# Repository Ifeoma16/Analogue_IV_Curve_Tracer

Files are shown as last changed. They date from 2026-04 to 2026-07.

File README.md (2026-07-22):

# Analogue I-V Curve Tracer Module




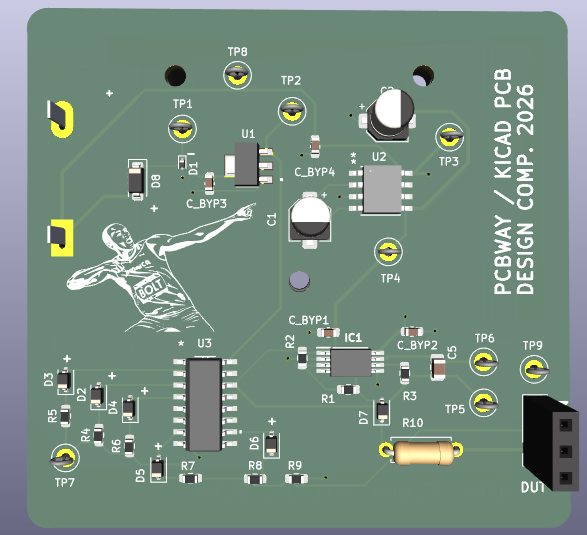
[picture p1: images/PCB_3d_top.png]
PCB_3D


An fully analogue evaluation module designed to generate characteristic I-V (current-voltage) curves for Devices Under Test (DUT) [resistors, capacitors, inductors, diodes, NPN, NMOS] using standard oscilloscope X-Y plotting. 

See Analogue_IV_Curve_Tracer.pdf file for full project report / datasheet

## 🚀 Overview
Unlike digital curve tracers, this design uses zero microcontrollers. It utilizes a synchronized hardware-only topology:
* **Base/Gate Drive:** A CD4017B decade counter configured for a 5-step staircase waveform.
* **Collector/Drain Sweep:** An op-amp integrator generating a continuous triangle wave (approx. 9V pk-pk).
* **Power Management:** 9V battery-powered with an integrated charge pump (ICL7660) for negative rail generation and ESD/Reverse Polarity protection.

---

## ✨ Key Features
- **Standalone Operation:** No firmware to flash; purely analog circuitry.
- **Precision Layout:** 4-layer PCB ($SIG \rightarrow GND \rightarrow GND \rightarrow SIG$) optimized for low-noise microamp-level current steps.
- **Multi-Component Support:** Optimized for NPN Transistors, NMOS, Diodes (including schottky, zener etc), Inductors, Capacitors, Resistors.
- **Reactive Analysis:** Capable of visualizing phase-shift loops in Capacitors and Inductors.

---

## 🛠 Hardware Specifications
| Parameter | Typical Value |
| :--- | :--- |
| **Supply Voltage** | 9V (Alkaline Battery) |
| **Sweep Frequency** | ~100 Hz |
| **Base Current Steps** | 5 Steps (approx. 10µA increments) |
| **PCB Dimensions** | 60mm x 60mm |
| **Layer Count** | 4 Layers |

---

## 📈 Sample Traces
| NPN Transistor | Capacitor (100μF) | Inductor (1H) |
| :---: | :---: | :---: |
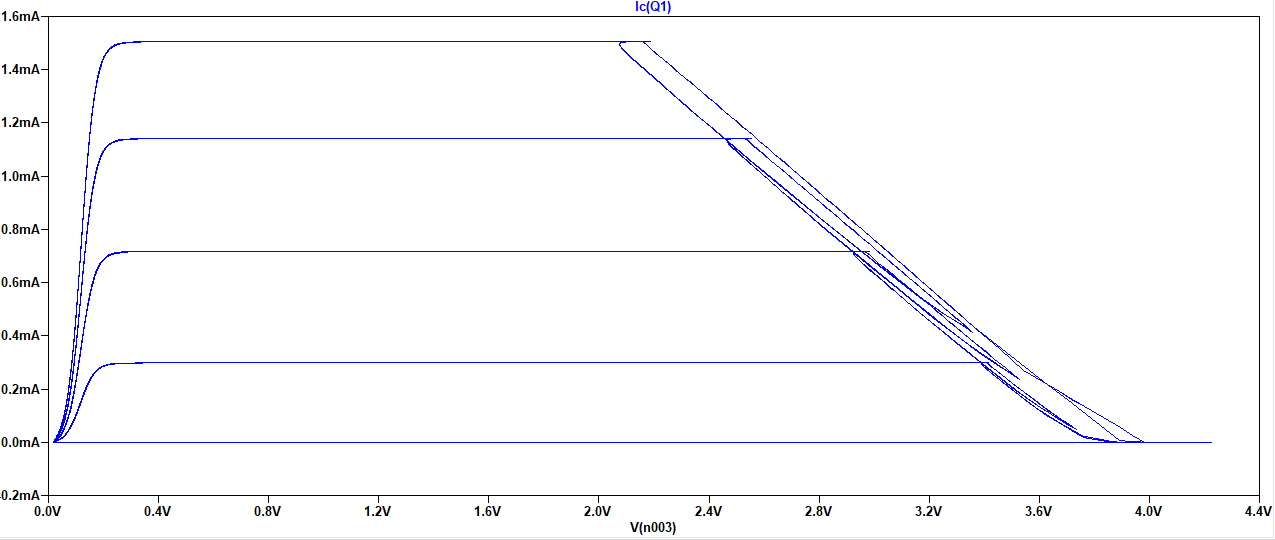
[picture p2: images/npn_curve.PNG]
NPN Trace
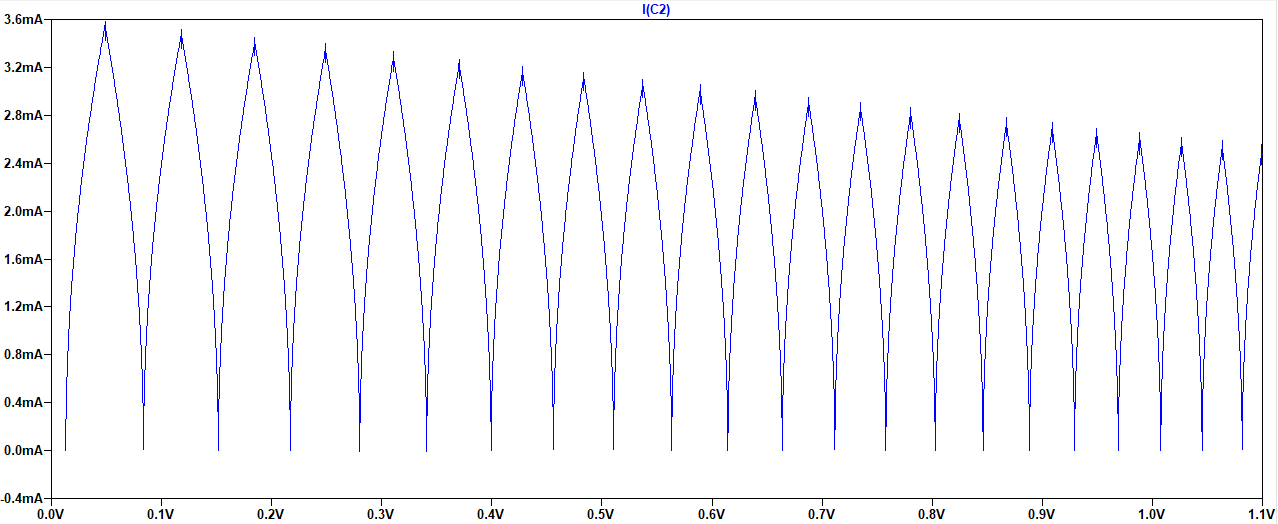
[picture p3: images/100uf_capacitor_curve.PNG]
Capacitor Trace
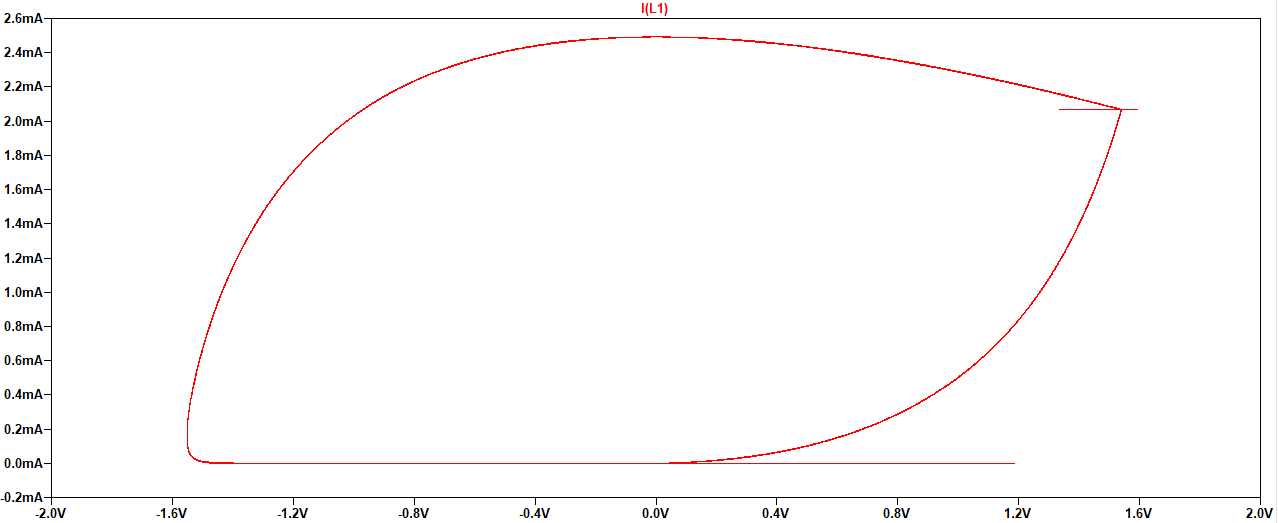
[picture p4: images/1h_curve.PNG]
Inductor Trace
|  |  |  |

---

## 🔌 Setup & Usage
To visualize curves on your oscilloscope:
1. **Power:** Connect a 9V battery to the onboard holder.
2. **Probing:** - Connect one probe (this will be X-axis) to the part of your DUT that is connected to pin 1.
   - Connect a clamp probe (this will be Y-axis)  around the wire or pin that connects your Device Under Test (DUT) to pin 1
3. **Scope Settings:** - Enable **X-Y Mode**.
   - Use XY mode to plot current vs. voltage
   - Ensure both ground clips are tied to the circuit ground.

---

## 📂 Repository Structure
* `/curve_tracer`: Full project files, including schematic, layout and fabrication files.
* `/resources`: PDFs I used for learning more on curve tracers.
* `/images`: All images used in datasheet and PCB.

---

## ⚠️ Design Limitations
- **Polarity:** This version is optimized for NPN and NMOS devices. PNP/PMOS devices will result in mirrored/inverted plots.
- **Power Dissipation:** Limited by the sourcing capability of the TL072H op-amps and the 1kΩ sense resistor.

---

## 🥚 Easter Egg
Look closely at the silkscreen: the module features **Usain Bolt**. Why? 

## 📜 References & Acknowledgments
Detailed resources used during the design phase (MIT reports, Op-amp integrator theory, etc.) are archived in the `/resources` folder.

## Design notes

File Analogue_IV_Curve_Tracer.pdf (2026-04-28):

Analogue I-V Curve Tracer Module | Rev 1.0

# Analogue I-V Curve Tracer Module

## 1 Features

- Standalone hardware topology (No MCU required)
- Synchronized 5-step staircase base current generator utilizing CD4017B logic
- Integrated triangle wave collector sweep
- 4-layer, low-noise PCB design (60mm × 60mm)
- Test Points accounted for on important nodes
- Battery holder for 9V alkaline battery
- Reverse polarity and ESD protection

## 2 Applications

- Discrete semiconductor characterization (NPN, NMOS, Diodes)
- Component matching and tolerance verification
- Educational laboratory demonstrations
- Reactive component (Capacitor/Inductor) loop analysis

## 3 General Description

The Analog I-V Curve Tracer is a compact evaluation module designed to generate standard characteristic curves for two- and three-terminal devices on any oscilloscope equipped with an X-Y mode. By utilizing a continuous triangle wave generated by an op-amp integrator and a decade counter used to generate a staircase wave, the module safely steps base current while sweeping collector voltage.
Note: Board can likely be made into 2-layers with ground plane on bottom if you would like, to save cost The 4-layer layout (SIG → GND → GND → SIG) aids signal integrity for microamp-level current steps. It is built to be powered by a 9V alkaline battery such as these (https://www.amazon.com/Amazon-Basics-Performance-All-Purpose-Batteries/dp/B00MH4QM1S?rdc=1) from Amazon.

There is a GitHub repository for this project, (https://github.com/Ifeoma16/Analogue_IV_Curve_Tracer) containing all files for the project.

Figure 0. Routing of the PCB


Figure 1. Top view of the 60x60mm assembled module.

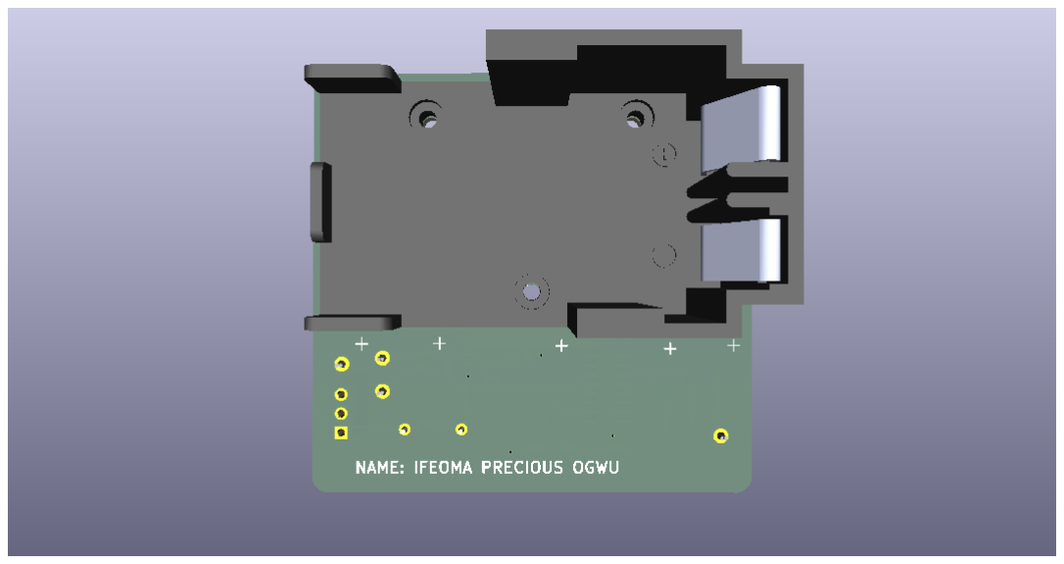
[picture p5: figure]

Figure 2. Bottom view of the 60x60mm assembled module.

## 4 Specifications

### 4.1 Absolute Maximum Ratings

Stresses beyond those listed may cause permanent damage to the device.

Parameter | Conditions | Max
Supply Voltage | Continuous | 9V
Module Power Dissipation | TA = 25◦C | 1.1 mW
DUT Power Dissipation | TA = 25◦C | 0.2 W

### 4.2 Electrical Characteristics

VCC = +9V, VEE = −9V, VDD = 5V, TA = 25◦C unless otherwise noted.

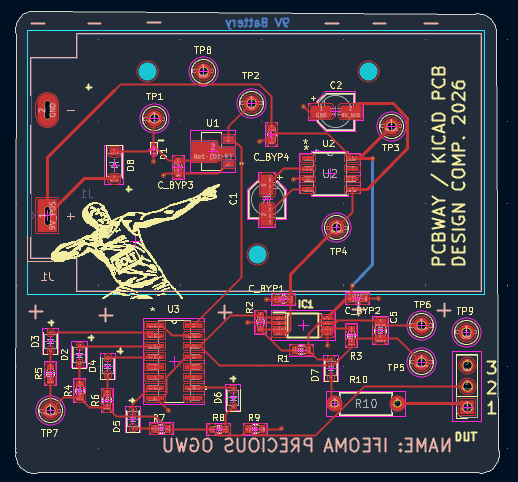
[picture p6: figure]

Ifeoma Precious Ogwu | 1 | PCBWay / KiCAD PCB Design Competition 2026

Parameter | Min | Typ | Max

Power Supply
Operating Voltage | 7V | 9V | 10V
Source Resistance | – | 55 | –
Quiescent Current | – | 2.4 mA | –

Sweep Generator
Sweep Freq. | – | 100Hz | –
Sweep Output (Vpk−pk) | – | 9V | –
Square Wave (Vpk−pk) | – | 16V | –

Base Drive
Number of Steps | – | 5 | –
Resistance | 450 | – | –
Capacitance | 10F | – | 1F
Inductance | 47mH | – | –

## 5 Detailed Description and Simulations

Simulations were conducted in LTSpice to validate design. A comparator op-amp circuit generates a 100Hz square wave that is fed into a comparator circuit generating a triangle wave. The op-amps used are the TL072H.

The square wave is fed into the clock signal of the CD4017B and the decade counter is used to generate the staircase wave. The staircase wave output is fed into a npn or NMOS (if that is the current DUT) through an external base / gate resistor.

The triangle wave is fed into a diode and resistor in series to pass only positive values of the triangle wave. This resistor connection is connected to the collector / drain of a npn or NMOS transistor of the top of a resistor, capacitor, inductor or positive side of a diode (schottky, zener etc) depending on the DUT.

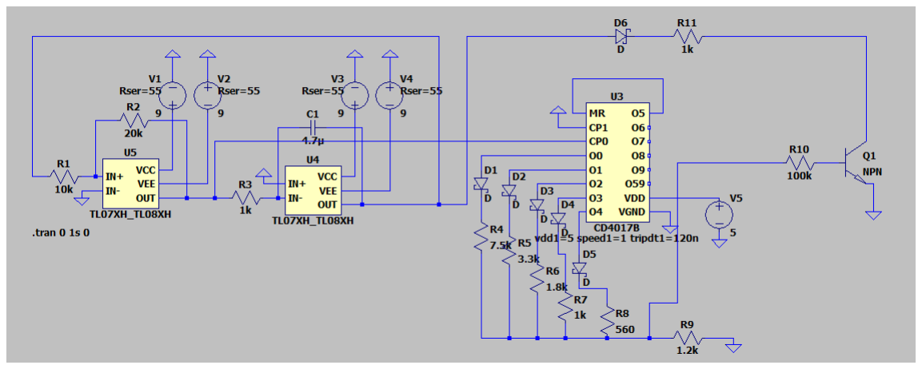
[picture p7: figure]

Figure 3. LTSpice Simulation.

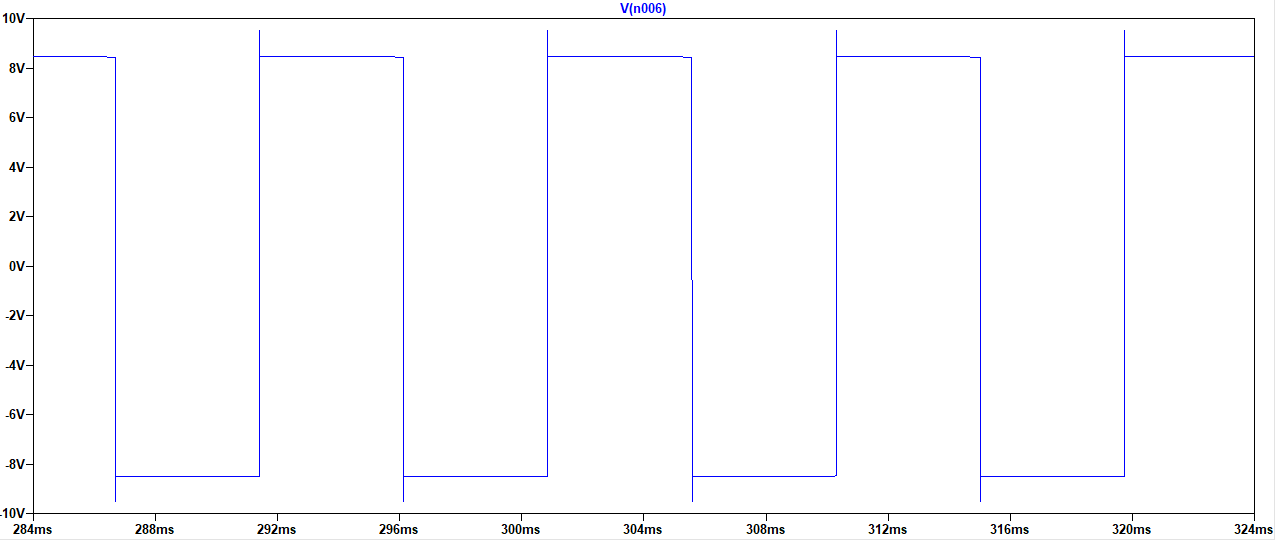
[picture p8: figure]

Figure 4. Square Wave From Simulation.

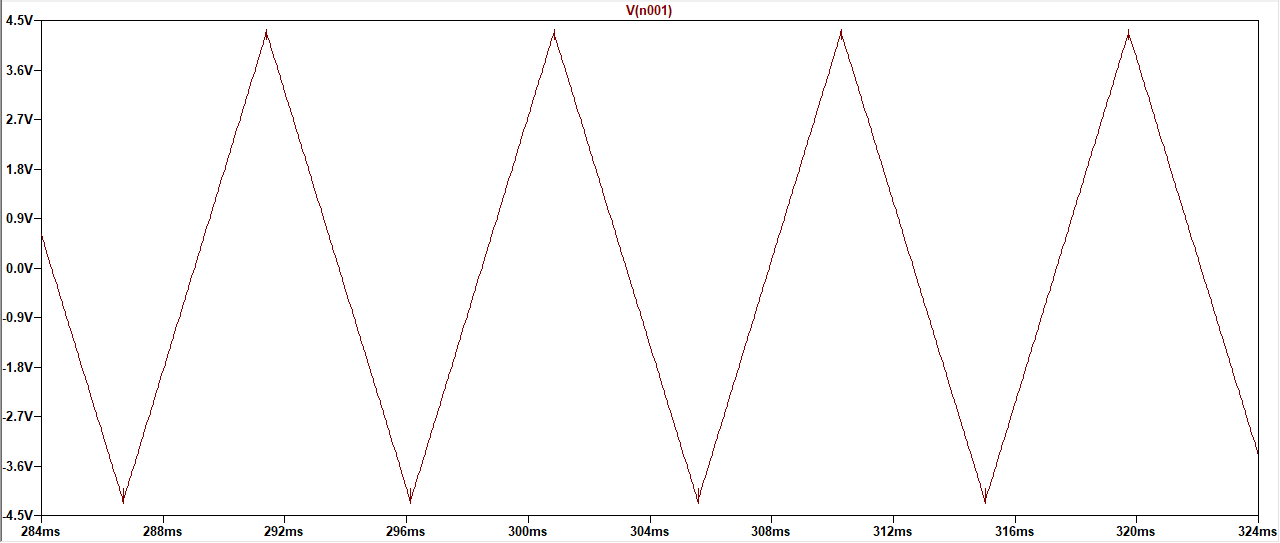
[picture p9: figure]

Figure 5. Triangle Wave From Simulation.

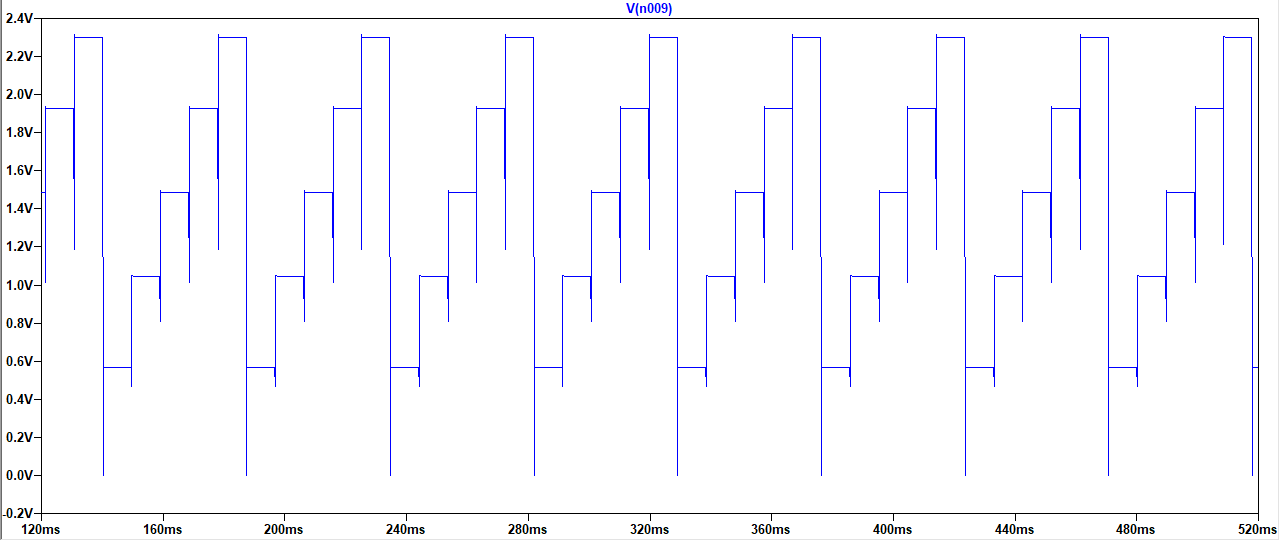
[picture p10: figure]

Figure 6. Staircase Wave From Simulation.

For the PCB:

The 9V battery is connected through a 1N5817 diode, used for reverse polarity protection, then a 11V TVS diode is connected from the cathode of 1N5817 to ground for ESD protection.
The line continues then to connect to the 5V LDO HT7350-A used to connect to VDD of the CD4017B. The 9V battery is also connected to an ICL7660 charge pump that gives us -9V which we can use ±9V for the op-amp. From there, the connections are basically same as in LTSpice. There are 0.1 bypass capacitors added to the input pins of the ICs to reduce / prevent noise.
The outputs of the entire circuit needed for the DUT is connected to a 3-pin 2.54mm header socket. There are also test points placed, that can be used for debugging or other purposes.

Note: There’s errors in DRC due to the components being on top of the battery holder. However, looking sideways, you can solder and cut the excess off enough to not interfere

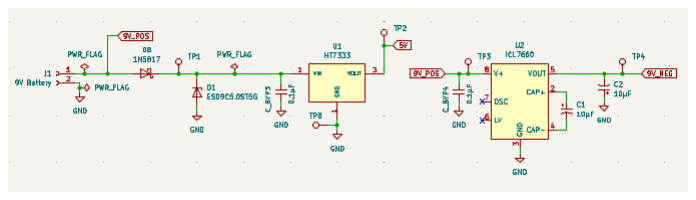
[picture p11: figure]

Figure 7. Positve and negative 9V generation, as well as 5V.

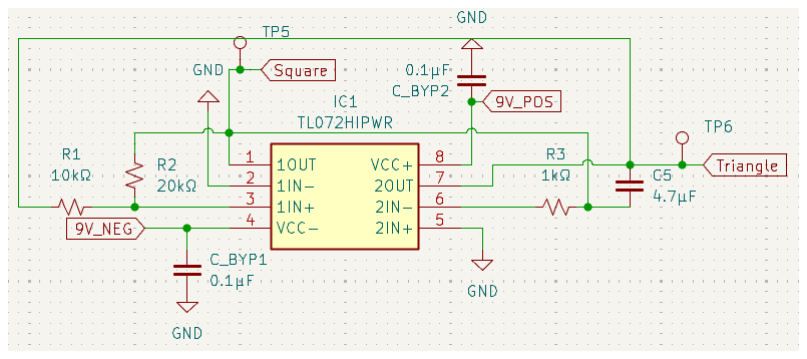
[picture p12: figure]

Figure 8. Square and triangle wave generation from op-amps.

Ifeoma Precious Ogwu | 2 | PCBWay / KiCAD PCB Design Competition 2026

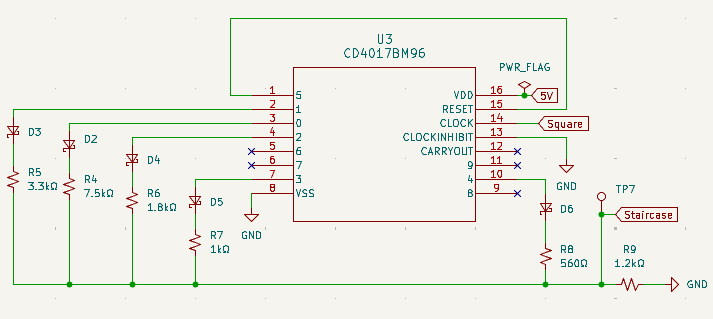
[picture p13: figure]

Figure 10. Staircase wave generation from decade counter.

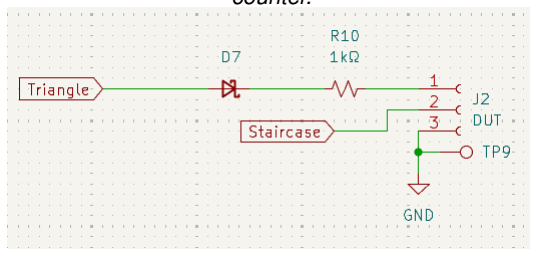
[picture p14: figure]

Figure 11. Outputs for DUT.

## 6 Naming

For use of this module, these are the relevant pins and their uses:
- TP1: 9V (positive). Placed in a such a way, it can be used to verify if the D8 is working properly and in right direction.
- TP2: 5V
- TP3: 9V (positive)
- TP4: 9V (negative)
- TP5: Square wave
- TP6: Triangle wave
- TP7: Staircase wave
- TP8: GND
- TP9: GND. This test point is located next to the DUT socket so you can use to ground your oscilloscope probe.

For the 3-pin socket that you can place your DUT into:

- 1: Connected to the series diode and 1k resistor connected from the triangle wave to the ”top” of the DUT
- 2: Staircase wave output. Use for NMOS and npn.
- 3: GND

## 7 Hardware Interface

How to connect each DUT:

### 7.1 Resistor

- Connect one end of the resistor to R10 and the other end to GND.

### 7.2 Capacitor

- Connect one end of the capacitor (if polarized, connect the positive) to R10 and the other end to GND

### 7.3 Inductor

- Connect one end of the inductor to R10 and the other end to GND.

### 7.4 Diode

- Connect the anode (positive) of the diode to R10 and the cathode (negative ) to GND.

### 7.5 npn

- Connect the collector to R10, connect the base to an external resistor which you then connect to pin 2 of the DUT socket, connect the emitter to GND.

### 7.6 NMOS

- Connect the drain to R10, connect the gate to an external resistor which you then connect to pin 2 of the DUT socket, connect the source to GND.

How to connect DUT to oscilloscope:

If you have a probe that can measure current such as this (https://www.amazon.com/Hantek-Transducer-Multimeter-Oscilloscope-Connector/dp/B08KZMS4Z2) (any products links in this document are not recommendations or endorsements [unless they are the ICs and components used in the PCB], they are simply examples) from Amazon then:

- Connect one probe (this will be X-axis) to the part of your DUT that is connected to pin 1.
- Connect a clamp probe (this will be Y-axis) around the wire or pin that connects your Device Under Test (DUT) to pin 1
- Use XY mode to plot current vs. voltage
- GND: Ensure oscilloscope ground clips are tied strictly to the board’s designated common ground to prevent shorting.

If you do not have a current clamp probe:

- Connect a small shunt resistor (eg 0.1 or 1) in series with pin 1 to your DUT. You maybe just use the on-board R10 as your shunt. This has not been tested yet, however.
- Connect a probe (this will be Y-axis) to one side of the resistor and the ground clip to the other. (Note: Ensure the ground clip is connected to the side closest to ground to avoid shorting your circuit, or use a differential measurement.)
- On the oscilloscope, use the Math function to divide the channel voltage by the shunt resistance value.
- Connect another probe (this will be X-axis) to the part of your DUT that is connected to pin 1.
- Use XY mode to plot current vs. voltage
- GND: Ensure oscilloscope ground clips are tied strictly to the board’s designated common ground to prevent shorting.
Ifeoma Precious Ogwu | 3 | PCBWay / KiCAD PCB Design Competition 2026

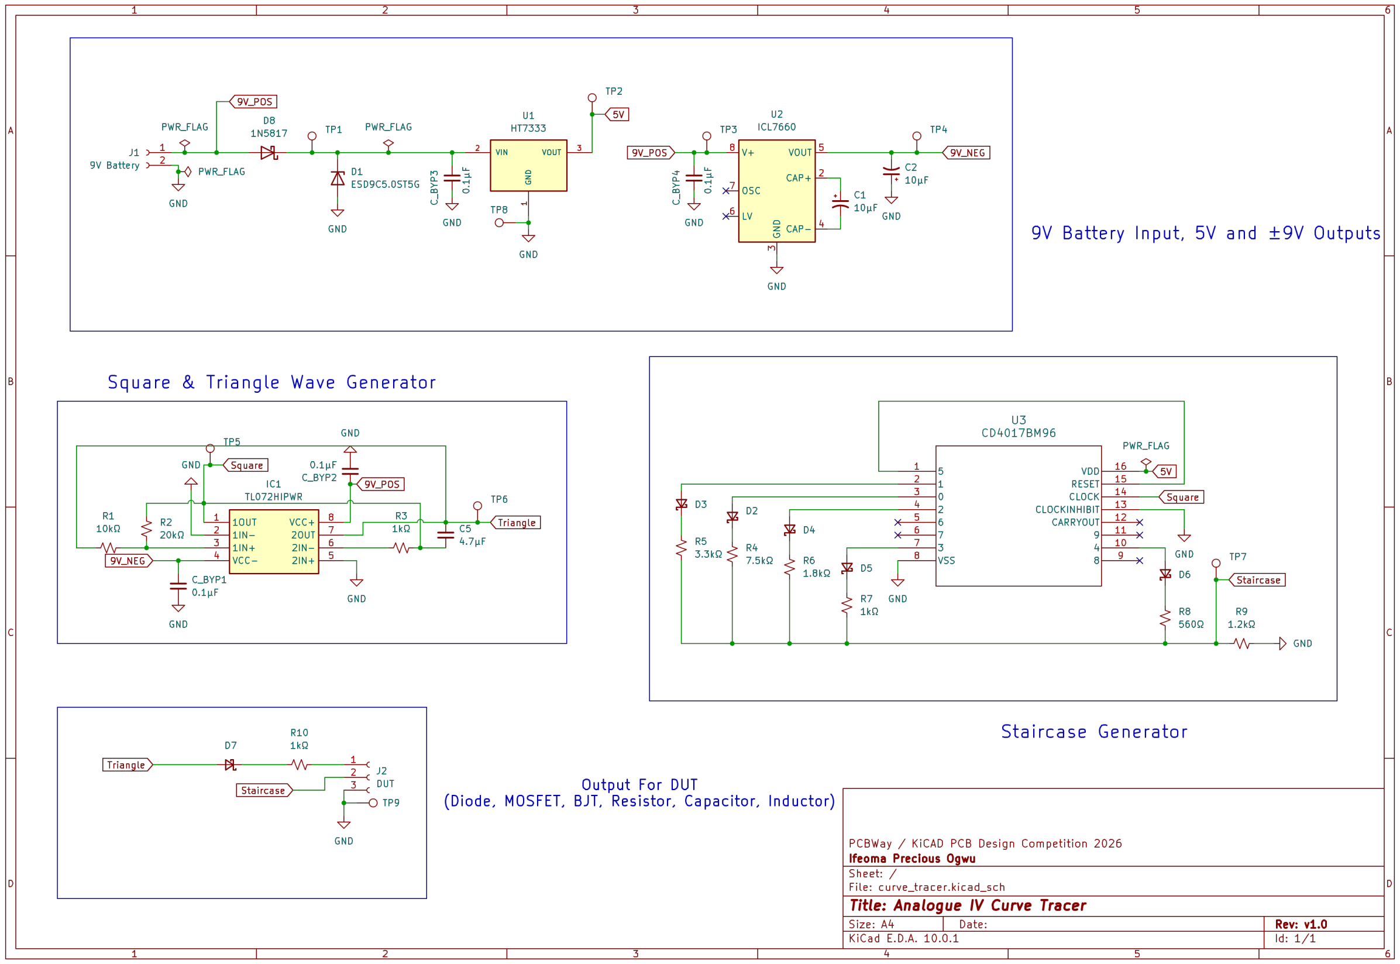
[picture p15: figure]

Figure 1: Figure 12. Full KiCAD Schematic

Ifeoma Precious Ogwu | 4 | PCBWay / KiCAD PCB Design Competition 2026

## Typical Performance Characteristics

The following waveforms represent typical operation using standard off-the-shelf components.


Figure 13. NPN Transistor Characteristic Sweep (Ic vs

Vce).

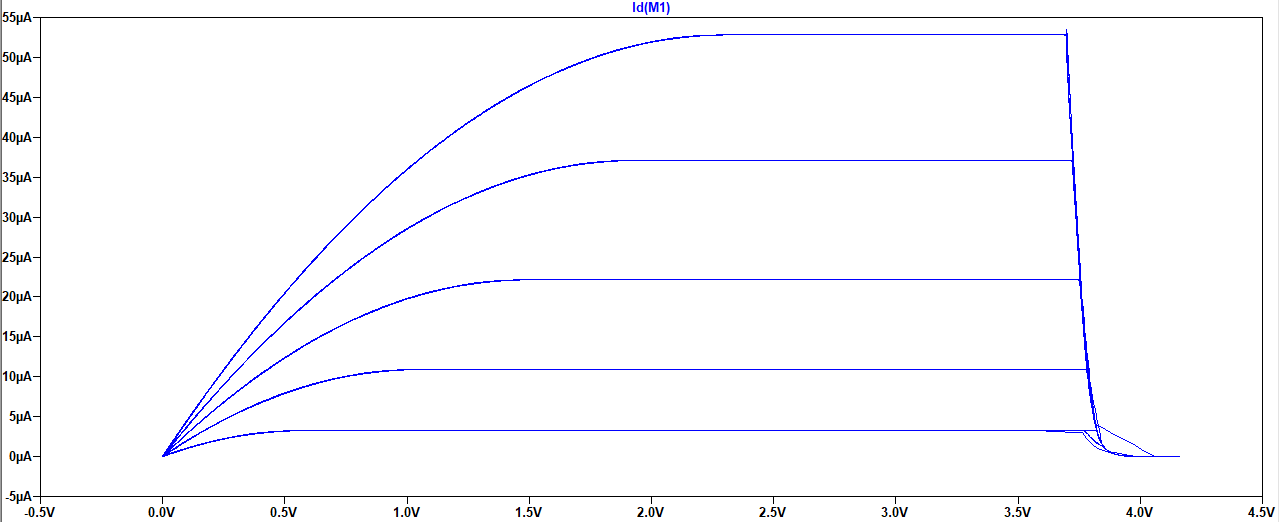
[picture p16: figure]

Figure 13. NMOS Transistor Characteristic Sweep (IG vs

VDS).


Figure 15. Reactive Load Analysis: 100µF Capacitor showing expected curve


Figure 16. Reactive Load Analysis: 1H Inductor showing standard elliptical response.

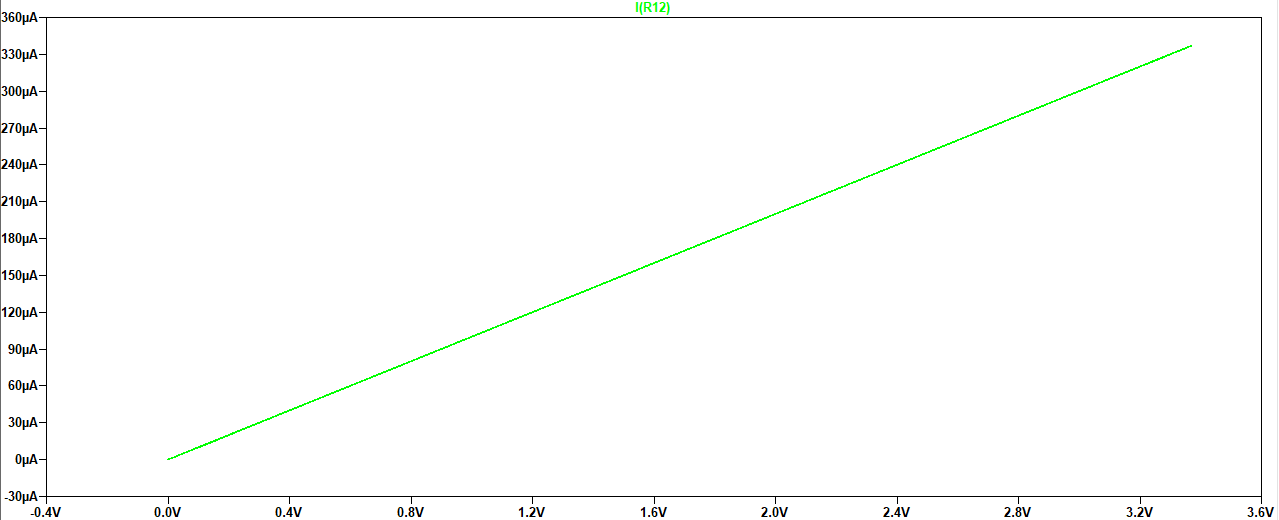
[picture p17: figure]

Figure 17. 10k resistor showing expected straight-line
graph.

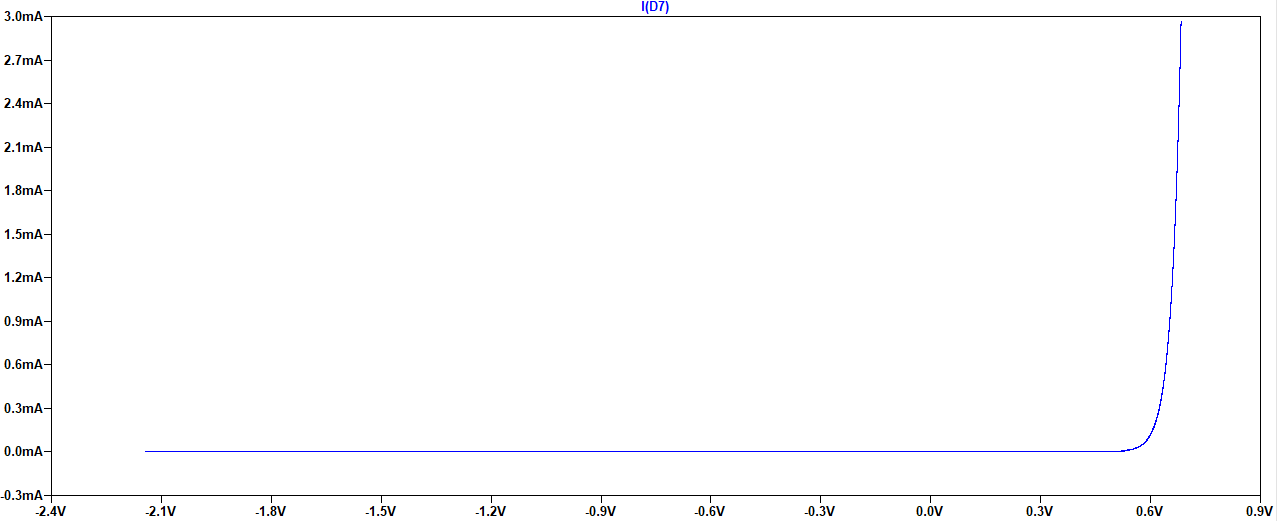
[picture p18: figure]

Figure 18. Diode showing expected curve.

Ifeoma Precious Ogwu | 5 | PCBWay / KiCAD PCB Design Competition 2026

## 8 BOM

The components were selected for a balance between high functionality and lower costs. The current BOM costs a total of $11.88 USD = 8.82 = 10.16 = $16.24 CAD = $207.24 MXN. The components were mainly sourced from DigiKey. There are also components sourced from LCSC and Amazon. You can source components from wherever you please, as long as it is the same footprint and make for the main ICs and as long as you are fine with your selected tolerances for capacitors and resistors.
Note: All resistors are 0.5W rated. You can get resistors rated for more power, but it is not recommended to get resistors rated for lower power.

The BOM is posted on the GitHub page for this project. (https://github.com/Ifeoma16/Analogue_IV_Curve_Tracer)

## 9 Design Limitations

While optimized for standard NPN and NMOS topologies, this hardware revision utilizes a unidirectional positive voltage sweep. Consequently, PNP and PMOS characterization will result in inverted/mirrored plots and may not fully forward-bias internal junctions correctly.
You are welcome to attempt to rectify this issue.

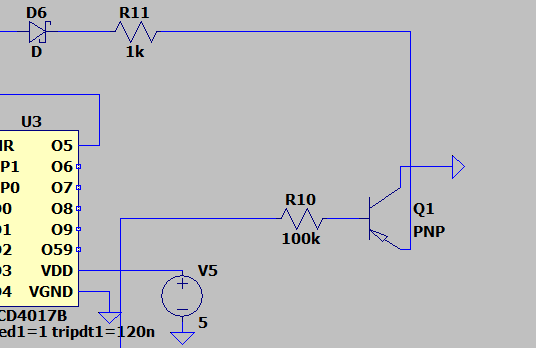
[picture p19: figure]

Figure 19. LTSpice Setup For pnp Or PMOS

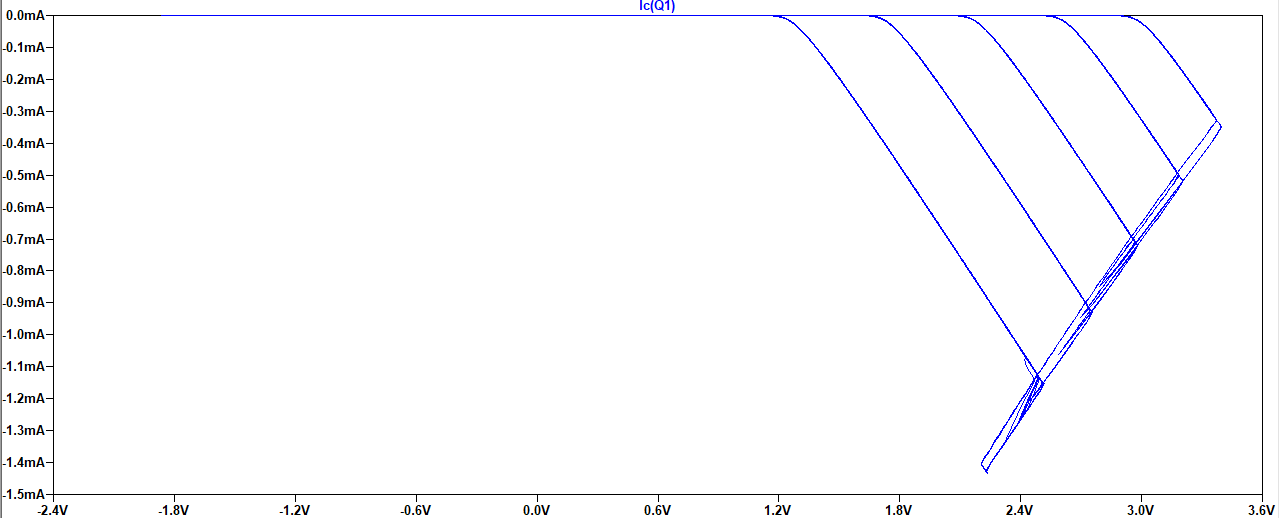
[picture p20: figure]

Figure 20. pnp curve.

Figure 21. PMOS curve.

Easter Egg: Why did I choose Usain Bolt specifically on my silkscreen?

## 10 Concluding Notes

Here are some of the resources I used to learn more about how to design and build a curve tracer:
- Building A Curve Tracer (https://www.paulvdiyblogs.net/2017/12/building-curve-tracer.html)
- Building A Curve Tracer v3 (https://www.paulvdiyblogs.net/2021/03/building-curve-tracer-version-3.html)
- Design & Build a Stair-Step Waveform Generator (http://www.scullcom.uk/design-build-a-stair-step-waveform-generator/)
- Analog Curve Tracer - MIT Report (https://web.mit.edu/6.101/www/s2020/projects/merni_Project_Final_Report.pdf)
- Op-Amp Comparator Circuit (https://www.electronics-tutorials.ws/opamp/op-amp-comparator.html)
- Op-Amp Integrator Circuit (https://www.electronics-tutorials.ws/opamp/opamp_6.html)

Most of the websites are in pdf format on the GitHub page for this project. (https://github.com/Ifeoma16/Analogue_IV_Curve_Tracer)

Using the online PCBWay instant quote:

For a PCBA, each board would cost about $29 Without PCBA, each board would cost about $17

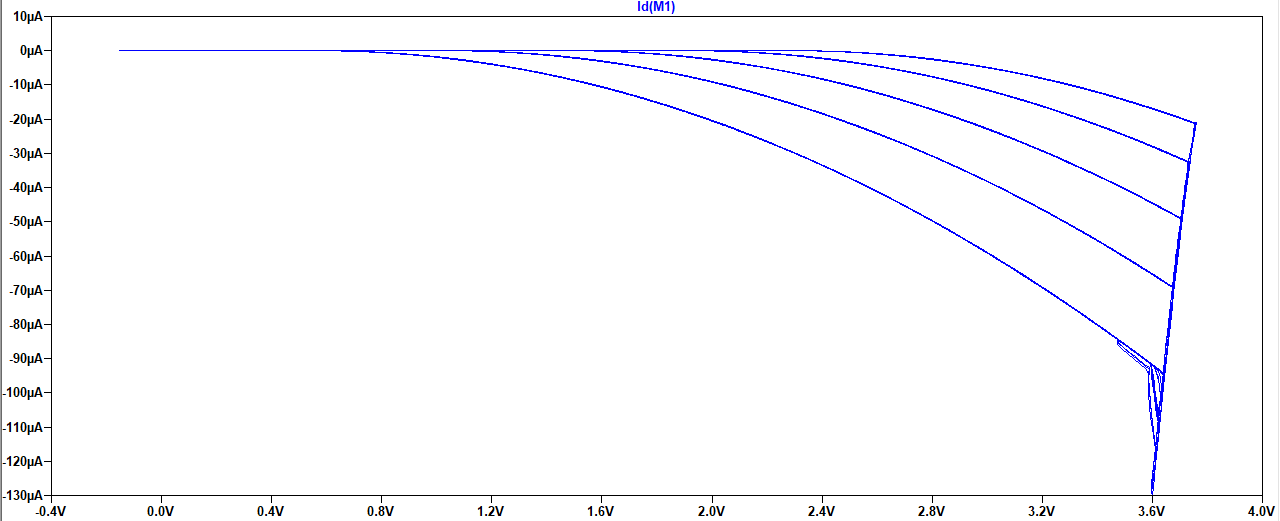
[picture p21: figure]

Ifeoma Precious Ogwu | 6 | PCBWay / KiCAD PCB Design Competition 2026

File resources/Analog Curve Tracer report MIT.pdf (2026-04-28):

# Analog Curve Tracer

### Makita Erni, Gregory Xie

### May 12, 2020

## Contents

1 Abstract | 3
2 Project Overview | 3
3 Design | 4

4 PCB Layout | 16
5 Conclusion | 21

## 1 Abstract

In order to preemptively replace the aging curve tracers in the 6.101 lab, we decided to design a replacement for our final project.

A replacement device should be able to replace the Tektronix 575 in the context of 6.101. This means that it has to be able to generate characteristic curves for BJTs and diodes. Users should be able to easily adjust testing parameters to fit the device being tested, and it should be easy to view and capture the generated curves.

Our design can automatically identify whether the device under test (DUT) is a bipolar junction transistor or a two-terminal device, like a resistor or a diode. If the device is a BJT, it also detects the type (NPN or PNP), as well as its orientation. Based off of this information, it sets up the test and applies the test currents in the appropriate directions. The BJT testing only works if the middle pin is the base, but that is usually the case, so it shouldn’t be a problem. Users can adjust various testing parameters through 3 rotary switches.

The output of the curve tracer can be read off of two test points and an oscilloscope in X-Y mode can be used to display the curves generated. This allows for the easy export of the characteristic curves through the oscilloscope’s USB port.

## 2 Project Overview

Our project’s circuit can be split into three main parts - the device identification circuit, the control voltage generation circuit, and the two voltage controlled current sources used to test the DUT.

The device identification circuit determines how the testing setup for the DUT should be setup, and includes an array of analog switches in order to connect the device in the way required for testing. The device identification circuit also provides the control voltage generation circuit with two voltages representing the directions of the base and collector currents.

The control voltage generation circuit uses these two voltages, as well as inputs given from the user through three rotary switches, to generate a staircase wave that controls the base current source, and a triangle wave that controls the collector current source. The commanded current is proportional to the voltage.

Finally, the two current sources reference the control voltages to test the DUT by pushing or pulling current through the device. Voltages representing the current through the device and the voltage across the device are available for the user to probe through test points.

## 3 Design

### 3.1 Overall System Design

The design involves a discrete sweep of the base current and a continuous sweep of the collector current which was accomplished with two voltage controlled current sources.

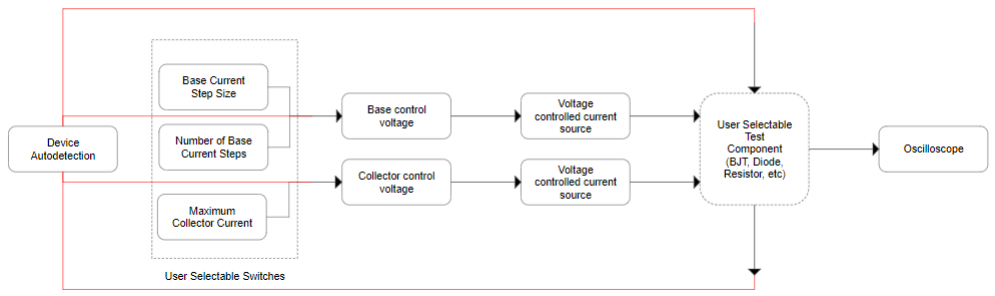
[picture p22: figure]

Figure 1: Overall Block Diagram

### 3.2 User Input

User input for setting the base current step size, number of base current steps, and the maximum collector current is taken through 10 position rotary switches. The switches for base current step size and maximum collector current change the gain of an amplification stage by changing the feedback resistor of an inverting amplifier. The switch for number of base current steps changes the value of a resistor in a voltage divider, changing a reference voltage.

### 3.3 Automatic Device Identification

### 3.3.1 Theory

This section of the circuit needs to determine if the DUT is a BJT or a two-terminal device, as well as determine the type and pin orientation for BJTs.

Because BJTs are constructed by sandwiching one semiconductor type between two layers of another, each has two junctions, and thus look like two diodes from the perspective of the base.

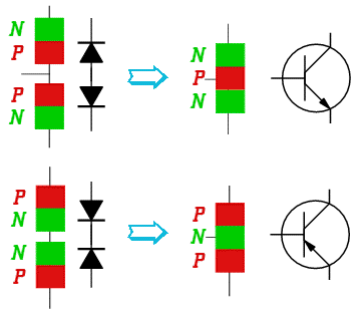
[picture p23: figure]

Figure 2: BJTs can be identified because they can look like two diodes from the perspective of the base. Source: http://fourier.eng.hmc.edu/e84/lectures/ch4/node3.html

A BJT can be identified by looking for these diode drops when the emitter and the collector are grounded through resistors, and a test voltage is applied to the base. For a PNP type BJT, the diode drops will appear when the test voltage is negative. For a NPN type BJT, the diode drops will appear when the test voltage is positive. When the test voltage is the wrong polarity for the type of device, the voltage drop will be the full test voltage. This allows for the identification of the type of device.

Because of differences in doping concentration (the emitter region is typically doped more heavily than the collector), the base-emitter diode drop is typically larger than the base-collector diode drop. This allows for the identification of these two pins.

Both of these methods require knowledge of which pin is the base of the device. Because this is the center pin for the BJT packages available in the lab, this was assumed to be known.

### 3.3.2 Implementation

The electronics that implement the device identification circuit consists of a sawtooth wave generator, window comparators, XOR gates, S/R latches, and opamp subtractors. The circuit controls an array of analog switches used to set up the testing conditions for the device.

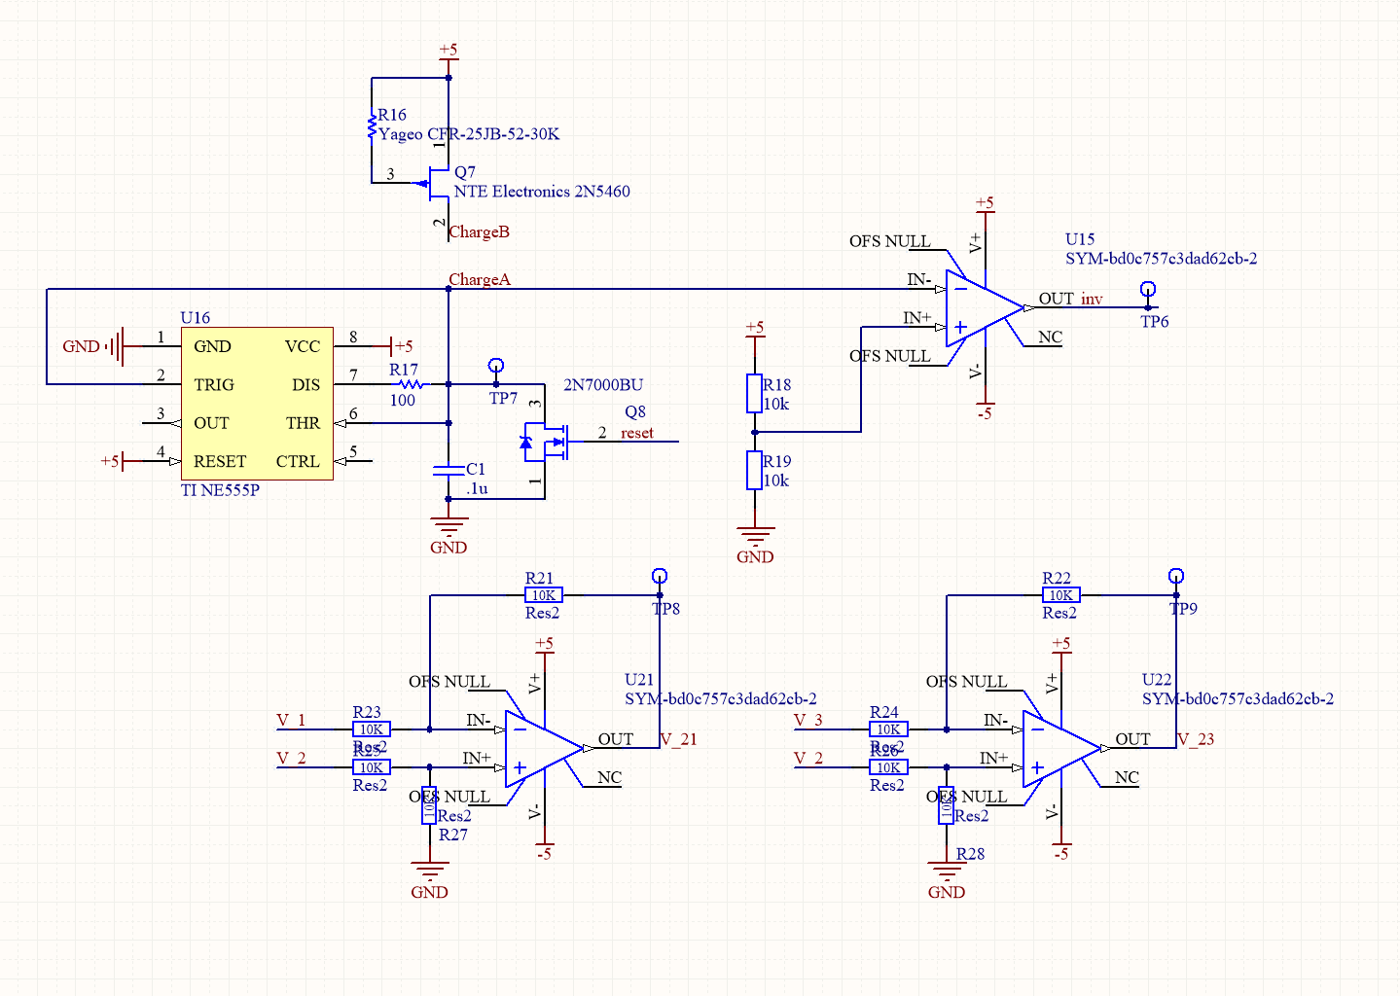
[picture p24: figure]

Figure 3: Sawtooth Generator, Subtractors, and Test Voltage Opamp

The sawtooth generator is implemented with a 555 timer set up in an astable configuration, with the timing capacitor driven by a JFET (2N54560) current source. The JFET current source is connected to the timing capacitor through an analog switch, which allows the circuit to hold the sawtooth voltage by disconnecting the current source. A NMOS (2N7000) connected in parallel with the timing capacitor allows the circuit to reset the sawtooth.

Each window comparator is made from two LM211s, which were chosen for their lower offset voltage when compared to the more common LM311. The reference voltages for the two comparators are set through a three tap resistor divider. By adjusting the values of the resistors in the divider, you can change the range of voltages in which the window comparator will output a logic high. As the output of the comparators are open-collector, they are pulled up to the positive supply rail through a resistor, and are tied together. The other comparators in the design are also LM211s.

Due to PCB size constraints, we opted to use integrated circuits to implement the XOR gates and S/R latches. For the XOR gates, the CD4043B was used, and for the S/R latch, the SN74LS86A was used. Both were chosen because they were not clocked, and were available in through hole packages. S/R latches were chosen instead of a sample-and-hold circuit because they were needed to reset the staircase wave used in the base control voltage, and many integrated circuits had multiple latches available. We can control when these latches sample the input by pulling the set pin to ground, and releasing it when we want to sample.

For the analog switches, we used the ADG441/ADG442 CMOS switches for all the switching where the resistance was not critical. These switches were used instead of MOSFETS because in a lot of the situations where switching is needed, the voltage at the source changes, which makes it hard to turn the MOSFET completely on. Using analog switches simplifies the

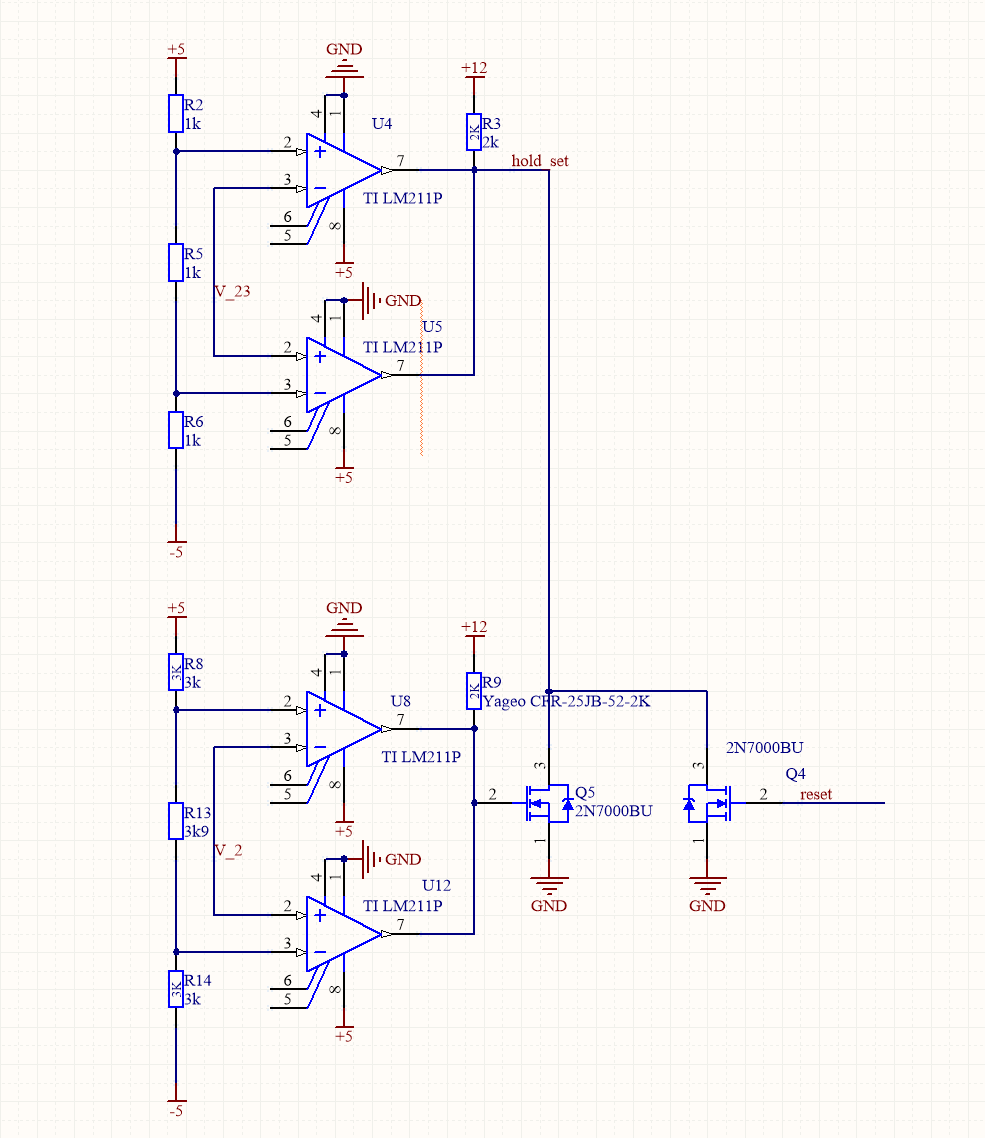
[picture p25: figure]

Figure 4: Window Comparator

design greatly, and allows us to switch both positive and negative voltages. To connect the DUT to our testing circuit, we used the MAX4663, which has a much lower on resistance (2.5 Ω), and guarantees break-before-make switching, allowing us to use them as multiplexers.

### 3.3.3 Operation

The sawtooth wave generator controls the entire device identification cycle, with different portions of the wave corresponding to different tests that the circuit performs. When the circuit has successfully identified a device, the circuit holds the sawtooth voltage constant while the device is being tested by disconnecting the JFET current source. Once testing is over, the sawtooth voltage is reset to 0 and the cycle restarts. Throughout the entire device identification cycle, the pins 1 and 3 are grounded through resistors. This is done through analog switches.

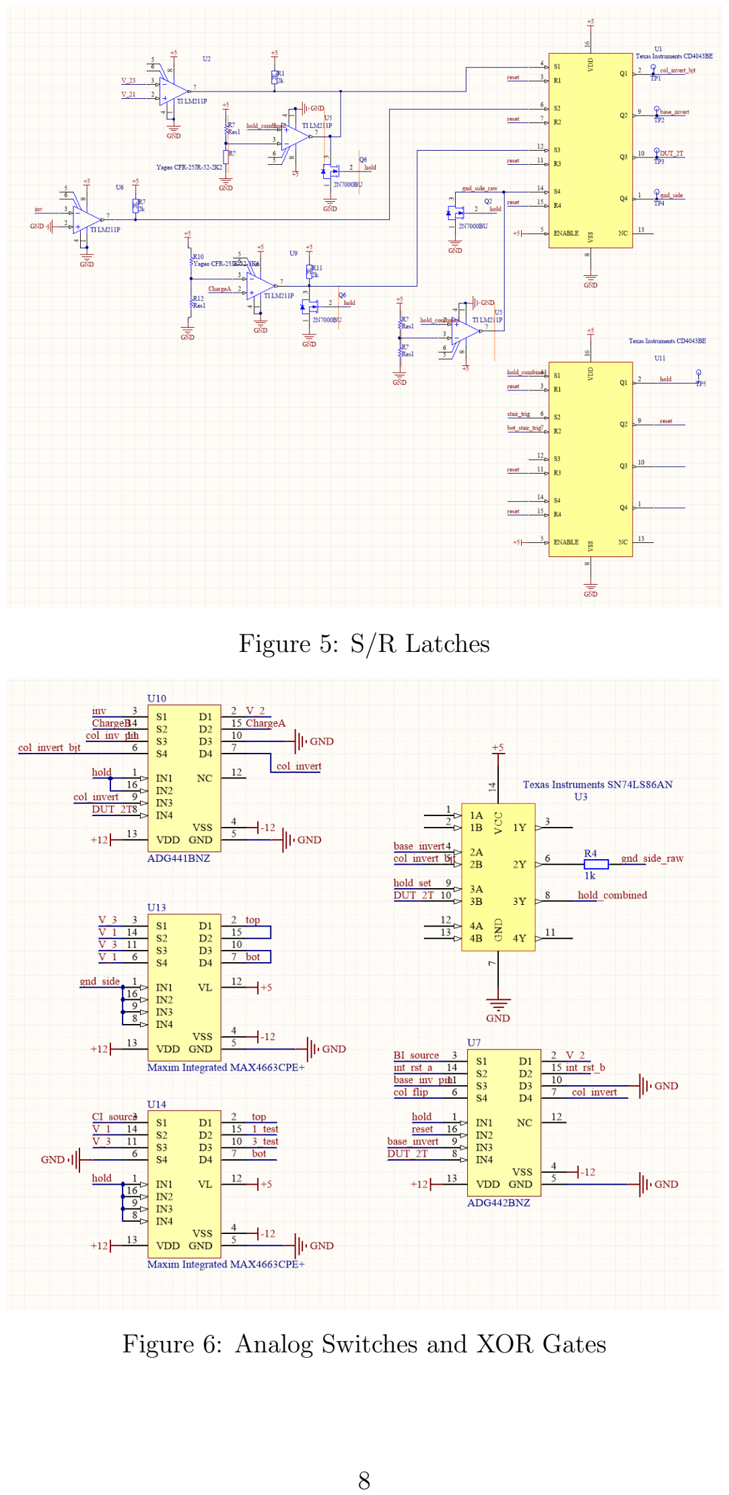
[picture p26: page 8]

Figure 5: S/R Latches

Figure 6: Analog Switches and XOR Gates

Throughout the entire testing period, the voltage drop between pins 2 and 3 (V2,3), as well as the voltage drop between 2 and 1 (V2,1) are measured. These two voltages are fed into a comparator that goes high when V2,1 > V2,3. This result can be XORed with the output of a comparator representing the inverse of the test voltage (high if negative test voltage, low if positive voltage) to produce a voltage which pin is the emitter of the device, which should be grounded during the testing cycle (GND Side). The inverse of the test voltage represents whether current should be pushed or pulled out of the base, as well as whether current should be pushed or pulled out of the collector. These values sampled and held in S/R latches when the device identification cycle ends and the testing cycle begins. These two voltages are used as inputs to an array of analog switches that connect the DUT to the testing setup in the correct way, and determine if the base and collector control voltages are inverted or not.

These relations can be seen in Table 1.

Device Identification Truth Table
V2,1 > V2,3 | Vtest < 0 | Collector and Base Current Direction | GND Side
1 1 0 0 | 1 (PNP) 0 (NPN) 1 (PNP) 0 (NPN) | 1 (Pull) 0 (Push) 1 (Pull) 0 (Push) | 0 (Pin 1) 1 (Pin 3) 1 (Pin 3) 0 (Pin 1)

Table 1: Truth Table relating measured values to testing parameters

For the first third of the sawtooth, the circuit checks to see if the DUT is a NPN BJT by applying 5V to pin 2. If −1.66 < V2,3 < 1.66, and (Vtest > 2 or Vtest < 2), the HOLD latch is set, the sawtooth voltage is held, and the device is tested using the parameters determined from the circuit. This ends the device identification cycle and starts the testing cycle.

For the middle third of the sawtooth, the circuit checks if the DUT is a PNP BJT by applying a negative voltage (-5V) to the base. V2,3 and the test voltage are checked again, and if the device passes, the device is tested.

If both of these tests fail, the sawtooth is allowed to reach its peak. When this happens, the device identification circuit assumes that the DUT is a two-terminal device. This sets a latch corresponding to this specific device type, which in turn connects the output pin of the 555 used for the triangle generation to the control pin of the analog switch used to invert the triangle wave. This inverts the control voltage waveform halfway through the sweep, switching the test current from positive to negative, and allowing for the full testing of diodes and resistors. When testing these devices, the middle pin remains unconnected.

### 3.4 Control Voltage Generation

The control voltage generation is accomplished by two parallel circuits, one that makes triangle waves for the collector current source, and one that makes a staircase wave for the base current source. Both of these circuits are triggered by a pulse generator, which allows the collector current sweeps to be aligned with a base current step.

### 3.4.1 Pulse Generator

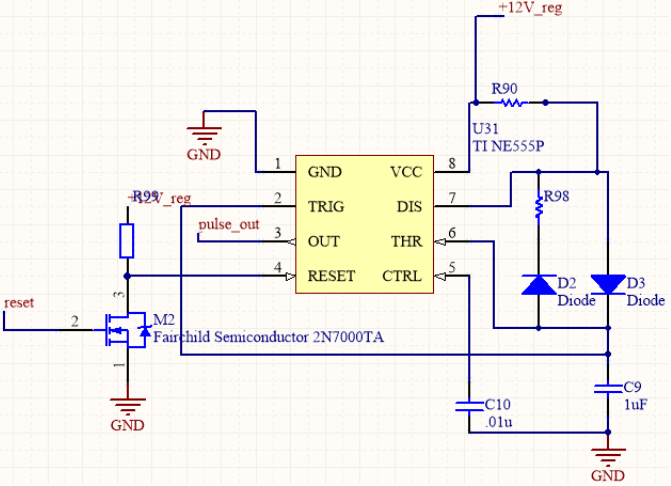
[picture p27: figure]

Figure 7: Pulse Generator Circuit

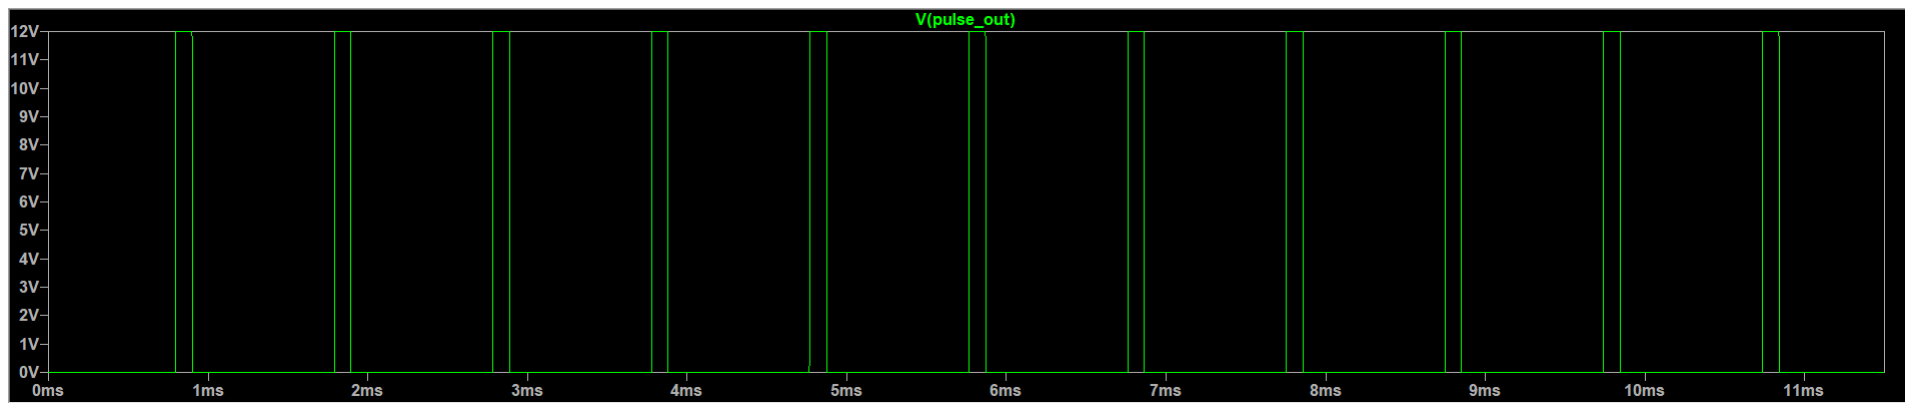
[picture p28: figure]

Figure 8: Pulse Generator Output Waveform

The pulse generator is implemented with an astable 555 timer circuit, with separate charging and discharging paths for the capacitor gated by diodes. This allows for a low duty cycle and easy control of the on and off times. The reset pin is held high when HOLD is high, signaling a testing cycle and enabling the 555 timer.

### 3.4.2 Staircase Wave Generation


Figure 9: Staircase Wave Generator Circuit


Figure 10: Example Staircase Waveform

The staircase wave is generated by integrating the pulses from the pulse generator using an opamp integrator. Once the staircase reaches a threshold voltage set by the user, the RESET S/R latch is set and the charge out of the integrating capacitor is drained out through an analog switch. When the voltage across the capacitor is close to 0V, the latch gets reset and the integrator is re-enabled. This allows the user to set the number of steps in the base current sweep.

Following the integrator, the wave goes through a unity-gain inverting/non-inverting opamp stage, where the wave can be inverted by pulling the non-inverting terminal of the opamp to ground. This stage is controlled by the device identification circuit through an analog switch. After this stage, the staircase goes through an inverting amplifier, where the gain is set by the user. This allows the user to control the size of the base current steps. The resulting waveform is fed to the base current source.

### 3.4.3 Triangle Wave Generation


Figure 11: Triangle Wave Generator Circuit


Figure 12: Example Triangle Wave

The triangle wave is generated using a monostable 555 timer circuit, with roughly equal charging and discharging times. One charge-discharge cycle of the timing capacitor happens in the period between pulses from the pulse generator. The pulses from the pulse generator are inverted and differentiated using an passive RC differentiator to act as the trigger for the circuit. This triggers the circuit on the falling edge of the pulse, which allows the base current to stabilize before the collector current sweep starts. The shape of this wave is not critical, and so a constant current source was not needed to charge the capacitor.

The output is taken across the timing capacitor, buffered and then sent through an identical set of processing stages. For the triangle wave, adjusting the gain of the inverting stage allows users to change the maximum current sent through the device.

### 3.5 Voltage Controlled Current Sources

The voltage controlled current sources consist of two circuits. One is connected to the pin 2 of the DUT and is controlled by the staircase wave generator. The other is connected to the collector of a BJT DUT or a pin on a two-terminal DUT and is controlled by the triangle wave generator.

### 3.5.1 Base Current Source

The base current source should discretely input different currents into pin 2 of the DUT. The step size and number of steps are set by the user input rotary switches.

The input from the Staircase Wave Generator will go into a Howland Current Pump which can sink or source up to 1.1mA of current depending on the input voltage.

Since the resistors in the Howland Current Pump have to be well matched, .1 percent tolerance resistors were chosen and spots for potentiometers in line with the resistors were added so the resistance could be precisely matched if the .1 percent tolerance was not tight enough.


Figure 13: Howland Current Pump

The current flowing out of R84 is the current flowing into pin 2 of the DUT. That current is the combination of the current flowing through R79 and R82. The Howland Current Pump adjusts the currents through R79 and R82 to keep the output current constant for each reference voltage input.

Figure 14: Example Base Current Staircase Wave

### 3.5.2 Collector Current Source

The collector current source should do a continuous sweep of different currents into the collector terminal of a BJT DUT. The max collector current is set by the user input rotary switches.

The input from the Triangle Wave Generator will go through an opamp into a pair of PNP and NPN BJTs in a push-pull configuration. The opamp will get feedback from an instrument amp measuring across a shunt resistor in the current path. This current source is able to source or sink up to 100mA of current depending on the input voltage.

The instrument amp is unity-gain. The original version of this system had some noise that was also getting amplified, so to reduce this the instrument amp gain was reduced, the OP27 was used because of its low noise characteristics, C5 and C7 were added to create a low pass filter, and a small R35 (30 ohms) was added to increase the damping ratio of the system.


Figure 15: Push-Pull Current Source

The negative feedback across the R32 which is the output resistor helps to ensure that the voltage across the resistor is the same as the triangle wave input voltage on the positive input pin of the op amp.

The voltage between pins 1 and 3 will be measured by measuring the collector voltage of the current source (Test Point 3) since the other pin is grounded. The current will be measured on the output of the instrument amp providing feedback to the collector current source (Test Point 2) using another oscilloscope probe.


Figure 16: Esample Collector Current Sweeps

Notice that it doesn’t always reach its peak. That is because it is limited by the ±15V rails.

## 4 PCB Layout

Because the maximum size for cheaply manufacturable PCBs is 10cm x 10cm, our entire design was unable to fit on one board. Instead, the design was split into two stacked PCBs, connected with a 16 pin header. Even though the design was spread over 2 PCBs, the top PCB is still completely filled with components, and the bottom PCB had to use SMD parts (1206) for the resistors used in the user input circuit in order for everything to fit on the bottom PCB.

The top PCB has the ±15V inputs, and linear regulators to make the ±5V and ±12V rails. It also contains the socket for the DUT, and the device identification circuit. This board has a cutout that the rotary switches can be accessed through.

The bottom PCB has the control voltage generators and the current sources, as well as the switches used for user inputs. There are test points acting as outputs for the oscilloscope at the back of the board.

### 4.1 Top PCB


Figure 17: Top PCB 3D View

While laying out and routing this board, care was taken to put the subtractors that made V2,3 and V2,1 as well as the comparator comparing these two values close to the DUT. For some devices, the difference between these two voltages can be only a couple of mV.

The 16 pin header would be soldered onto the board such that the pins were facing down to interface with the bottom PCB.


Figure 18: Top PCB Top Layer

Figure 19: Top PCB Bottom Layer

### 4.2 Bottom PCB


Figure 20: Bottom PCB 3D View

The test points would likely be rotated 90 degrees from how they are shown in this CAD model for ease of connection. Test Point 1 is a ground.


Figure 21: Bottom PCB Top Layer

Figure 22: Bottom PCB Bottom Layer

## 5 Conclusion

As is, the project works as expected in simulation. The generated characteristic curves are readable, with some small artifacts.

### 5.1 Challenges

1. LTSpice can be tempermental and can also take a lot of time to simulate, so some design and component choices were made because they caused the simulation to run the fastest and most consistently. This was especially important for the final project this year because our entire design had to work in simulation.
2. Integrating automatic device detection with the rest of the circuit was difficult, as the test device has to switch between being connected to the detection circuit, and the testing circuit. This caused lots of problems with the simulation.

### 5.2 Improvements

In simulation, our design works as is, but there are some improvements that would have been implemented if there was more time and board space.

1. Add a boost power supply to increase the voltage rails.

In our current design, the highest voltage that can be applied to a device is 15V. By implementing a boost power supply, the curve tracer would be able to apply higher voltages to the DUT, allowing larger current sweeps.

2. Add potentiometers to trim the base control voltage generator.

Currently, there is no way for the user to adjust the values of the passive components used in the control voltage generation circuit without replacing the components out-right. This does not matter much for the collector control voltage, but can influence the size of the base current control voltage steps. When calculating the β of a device, this can introduce error.

3. Bus capacitors for the collector current source.

The amount of current that the collector current source provides changes at around 1 KHz, and can introduce noise into the power rails. By adding bus capacitors close to the current source, they act as local energy sources, reducing the voltage fluctuations on the power rails.

### 5.3 Simulation Results

Many of the characteristic curves have artifacts from the connection and disconnection of the current sources from the DUT.

5.3.1 2N3904


Figure 23: 2N3904 Characteristic Curves

5.3.2 2N3906


Figure 24: 2N3906 Characteristic Curves

5.3.3 1N914


Figure 25: 1N914 Characteristic Curve

5.3.4 10 Ohm Resistor


Figure 26: 10 Ohm Resistor Characteristic Curve

### 5.3.5 Link To Testing Video

Full:

http://dropbox.com/6.101FinalProjectTesting (https://www.dropbox.com/s/u2gq7u1wxwhrqn8/video_good.mov?dl=0)

8 Times Speed:

http://dropbox.com/6.101FinalProjectTesting8x (https://www.dropbox.com/s/83oie4vsfgg57w8/video_good_8x_highq.mp4?dl=0)

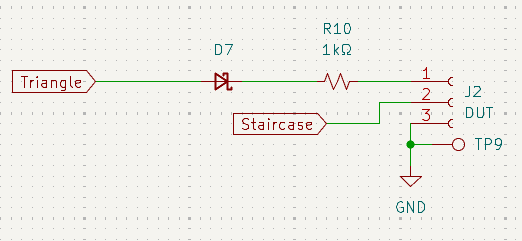
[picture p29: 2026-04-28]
images/outputs_schematic.PNG

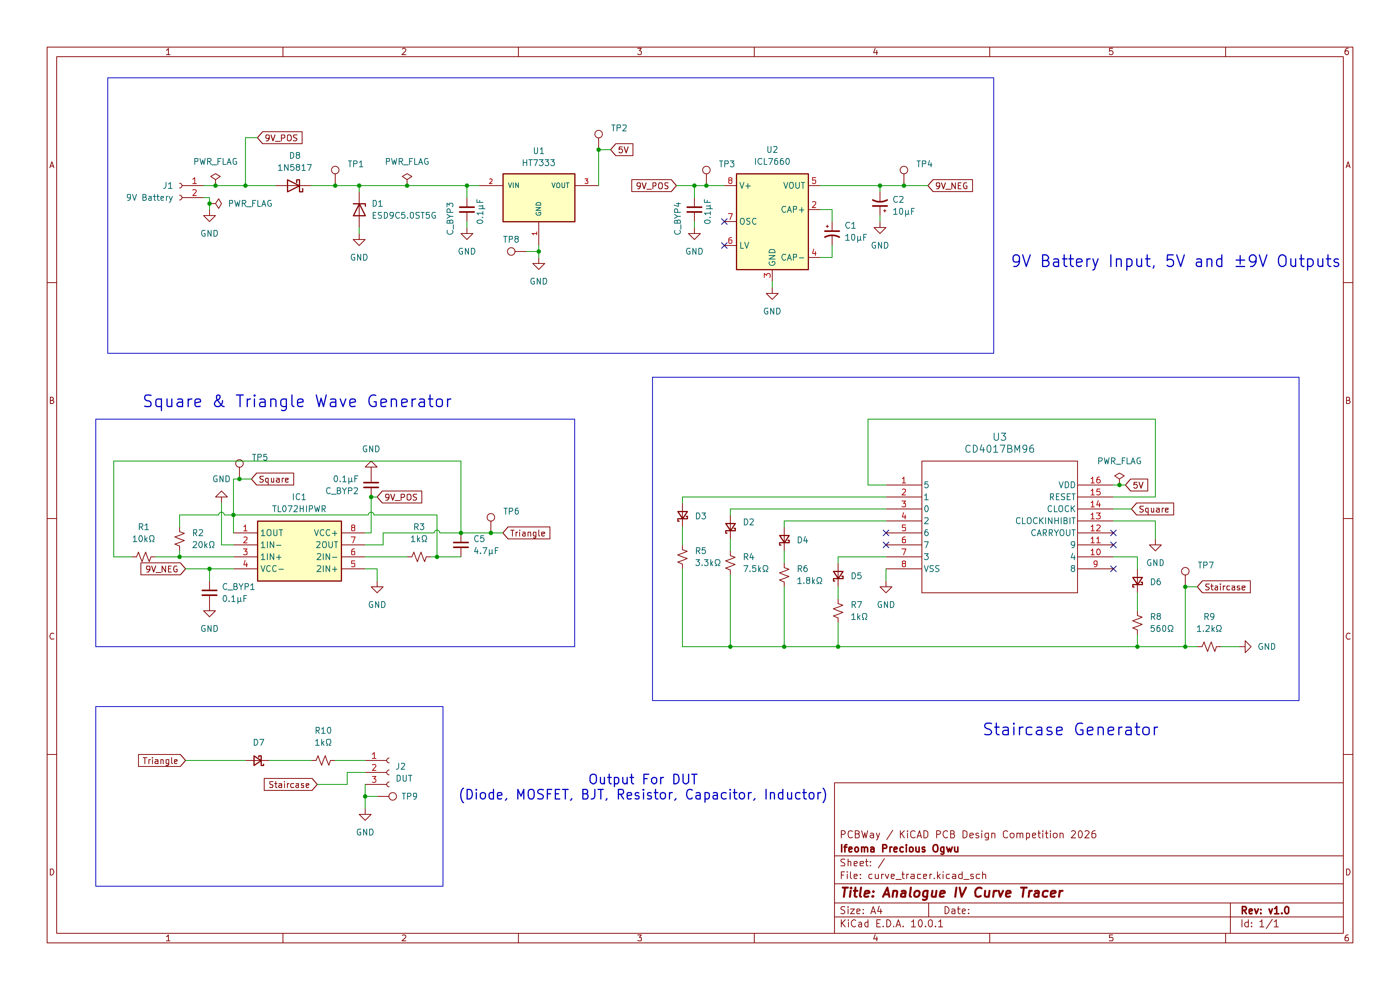
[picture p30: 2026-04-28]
images/full_schematic.png

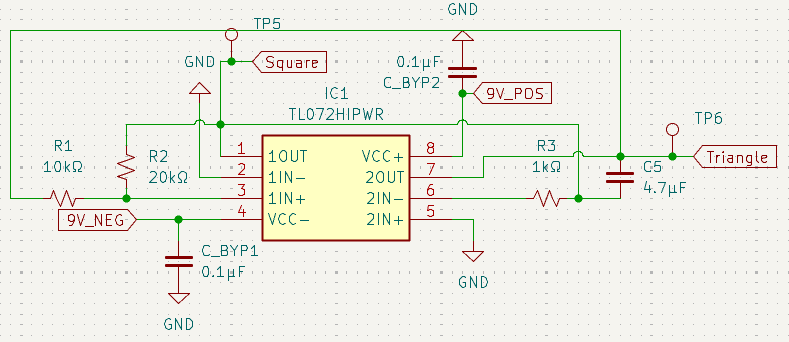
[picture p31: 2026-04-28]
images/square_triangle_wave.PNG

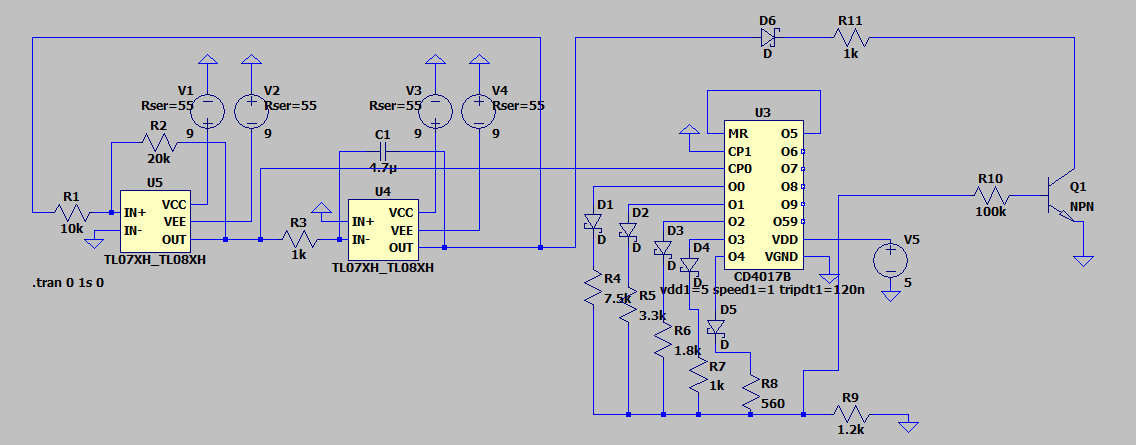
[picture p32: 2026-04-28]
images/ltspice_simulation.PNG

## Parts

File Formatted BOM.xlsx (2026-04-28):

Reference | Qty | Value | MFN | Unit Price | Link | Footprint
C1,C2 | 2 | 10µF | 865080340001 | $0.18 | 865080340001 (https://www.digikey.com/en/products/detail/w%C3%BCrth-elektronik/865080340001/5728006) | Capacitor_SMD:CP_Elec_4x5.8
C_BYP1,C_BYP2,C_BYP3,C_BYP4 | 4 | 0.1µF | C0603C104K4RACTU | $0.10 | C0603C104K4RACTU (https://www.digikey.com/en/products/detail/kemet/C0603C104K4RACTU/411095) | Capacitor_SMD:C_0402_1005Metric
C5 | 1 | 4.7µF | HRE CSA0805X7R475K160MT | $0.0189 | HRE CSA0805X7R475K160MT (https://www.lcsc.com/product-detail/C5254897.html) | Capacitor_SMD:C_0805_2012Metric
D1 | 1 | ESD9C5.0ST5G | ESD9C5.0ST5G | $0.30 | ESD9C5.0ST5G (https://www.digikey.com/en/products/detail/onsemi/ESD9C5-0ST5G/1646451) | Diode_SMD:D_SOD-923
D2,D3,D4,D5,D6,D7 | 6 | D_Schottky_Small | CUS15S30,H3F | $0.34 | CUS15S30,H3F (https://www.digikey.com/en/products/detail/toshiba-semiconductor-and-storage/CUS15S30-H3F/5114301) | Diode_SMD:D_SOD-323
IC1 | 1 | TL072HIPWR | TL072HIPWR | $0.31 | TL072H (https://www.digikey.com/en/products/detail/texas-instruments/TL072HIPWR/15212754?s=N4IgTCBcDaIC4BsAMB2MALAlgBwO4CcQBdAXyA) | TL072HIPWR:SOP65P640X120-8N
J1 | 1 | 9V Battery | BA9VPC | $2.50 | BA9VPC (https://www.digikey.com/en/products/detail/mpd-memory-protection-devices/BA9VPC/2439228?s=N4IgTCBcDaIEIEECcA1ACgYRAXQL5A) | Battery:BatteryHolder_MPD_BA9VPC_1xPP3
J2 | 1 | DUT | Chanzon Pin Header Strip | $0.14 | Amazon (https://www.amazon.com/Chanzon-Straight-Connector-Breadboard-Electronic/dp/B09MYMD4YS) | Connector_PinSocket_2.54mm:PinSocket_1x03_P2.54mm_Vertical
R1 | 1 | 10kΩ | RCS060310K0FKEA | $0.14 | RCS060310K0FKEA (https://www.digikey.com/en/products/detail/vishay-dale/RCS060310K0FKEA/5866941) | Resistor_SMD:R_0603_1608Metric
R2 | 1 | 20kΩ | RCS060320K0FKEA | $0.14 | RCS060320K0FKEA (https://www.digikey.com/en/products/detail/vishay-dale/RCS060320K0FKEA/5866943) | Resistor_SMD:R_0603_1608Metric
R3,R7 | 2 | 1kΩ | SG73P1JTTD1001F | $0.12 | SG73P1JTTD1001F (https://www.digikey.com/en/products/detail/koa-speer-electronics-inc/SG73P1JTTD1001F/10188084) | Resistor_SMD:R_0603_1608Metric
R4 | 1 | 7.5kΩ | RCS06037K50FKEA | $0.14 | RCS06037K50FKEA (https://www.digikey.com/en/products/detail/vishay-dale/RCS06037K50FKEA/5868579) | Resistor_SMD:R_0603_1608Metric
R5 | 1 | 3.3kΩ | RCS06033K30FKEA | $0.14 | RCS06033K30FKEA (https://www.digikey.com/en/products/detail/vishay-dale/RCS06033K30FKEA/5868540) | Resistor_SMD:R_0603_1608Metric
R6 | 1 | 1.8kΩ | RCS06031K80FKEA | $0.14 | RCS06031K80FKEA (https://www.digikey.com/en/products/detail/vishay-dale/RCS06031K80FKEA/5868511) | Resistor_SMD:R_0603_1608Metric
R8 | 1 | 560Ω | RCS0603560RFKEA | $0.14 | RCS0603560RFKEA (https://www.digikey.com/en/products/detail/vishay-dale/RCS0603560RFKEA/5868457) | Resistor_SMD:R_0603_1608Metric
R9 | 1 | 1.2kΩ | RCS06031K20FKEA | $0.13 | RCS06031K20FKEA (https://www.digikey.com/en/products/detail/vishay-dale/RCS06031K20FKEA/5868493) | Resistor_SMD:R_0603_1608Metric
R10 | 1 | 1kΩ | MFR50SFTE52-1K | $0.10 | MFR50SFTE52-1K (https://www.digikey.com/en/products/detail/yageo/MFR50SFTE52-1K/9151157) | Resistor_THT:R_Axial_DIN0207_L6.3mm_D2.5mm_P7.62mm_Horizontal
TP1,TP2,TP3,TP4,TP5,TP6,TP7,TP8,TP9 | 9 | TestPoint | Comimark | $0.07 | Amazon (https://www.amazon.com/Comimark-100Pcs-Black-Soldering-Breadboard/dp/B07X32N4YJ) | TestPoint:TestPoint_Loop_D2.50mm_Drill1.0mm_LowProfile
D8 | 1 | 1N5817 | 1N5817W | $0.10 | 1N5817W (https://www.digikey.com/en/products/detail/shenzhen-slkormicro-semicon-co-ltd/1N5817W/25701312) | Diode_SMD:D_SOD-123
U1 | 1 | HT7350-A | HT7350-A | $0.42 | HT7350-A (https://www.digikey.com/en/products/detail/umw/HT7350-A/17635221) | Package_TO_SOT_SMD:SOT-223-3_TabPin2
U2 | 1 | ICL7660SCBAZ-T | ICL7660SCBAZ-T | $2.71 | ICL7660SCBAZ-T (https://www.digikey.com/en/products/detail/renesas-electronics-corporation/ICL7660SCBAZ-T/1034515) | Custom_miscellaneous_v10:ICL7660
U3 | 1 | CD4017BM96 | CD4017BM96 | $0.69 | CD4017B (https://www.digikey.com/en/products/detail/texas-instruments/CD4017BM96/1690809) | CD4017BM96:D16
 |  |  | Component Total: | $11.88
 |  |  | PCBWay Quote (No PCBA) | $5.20 | Per Board
 |  |  | PCBWay Quote (With PCBA) | $11.00 | Per Board
 |  |  | Grand Total (No PCBA): | $17.08
 |  |  | Grand Total (With PCBA): | $28.97

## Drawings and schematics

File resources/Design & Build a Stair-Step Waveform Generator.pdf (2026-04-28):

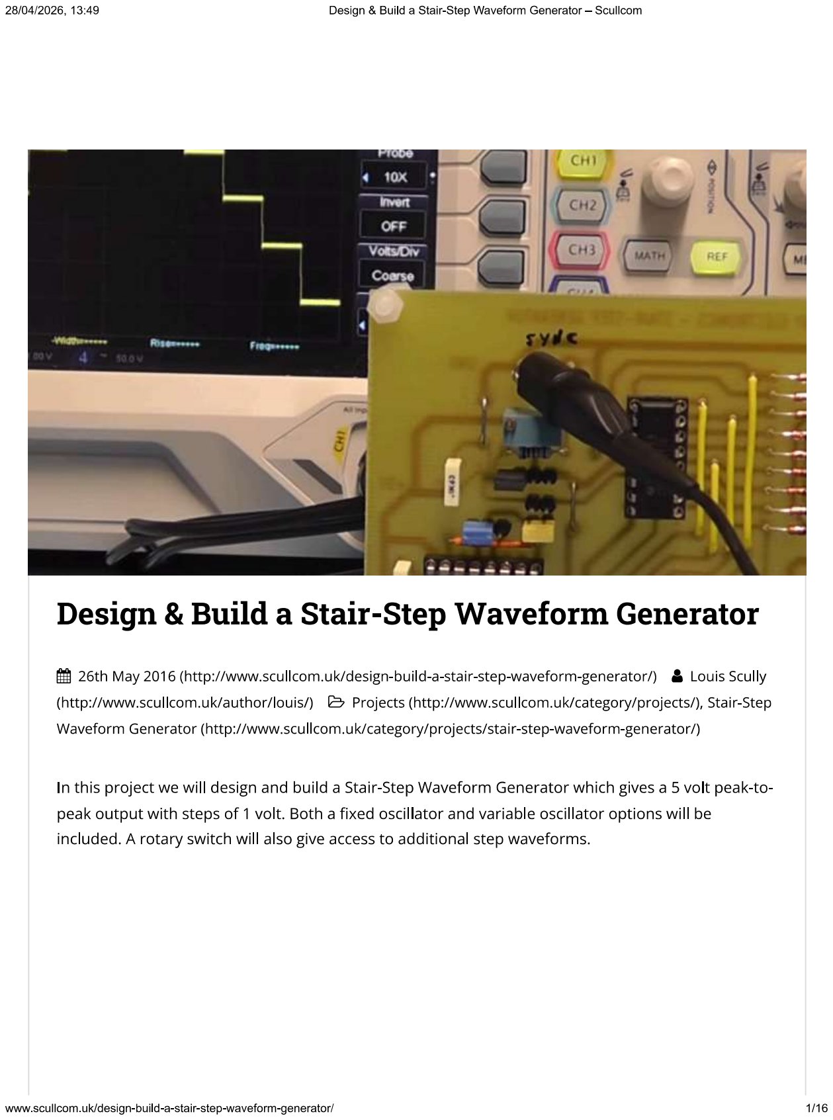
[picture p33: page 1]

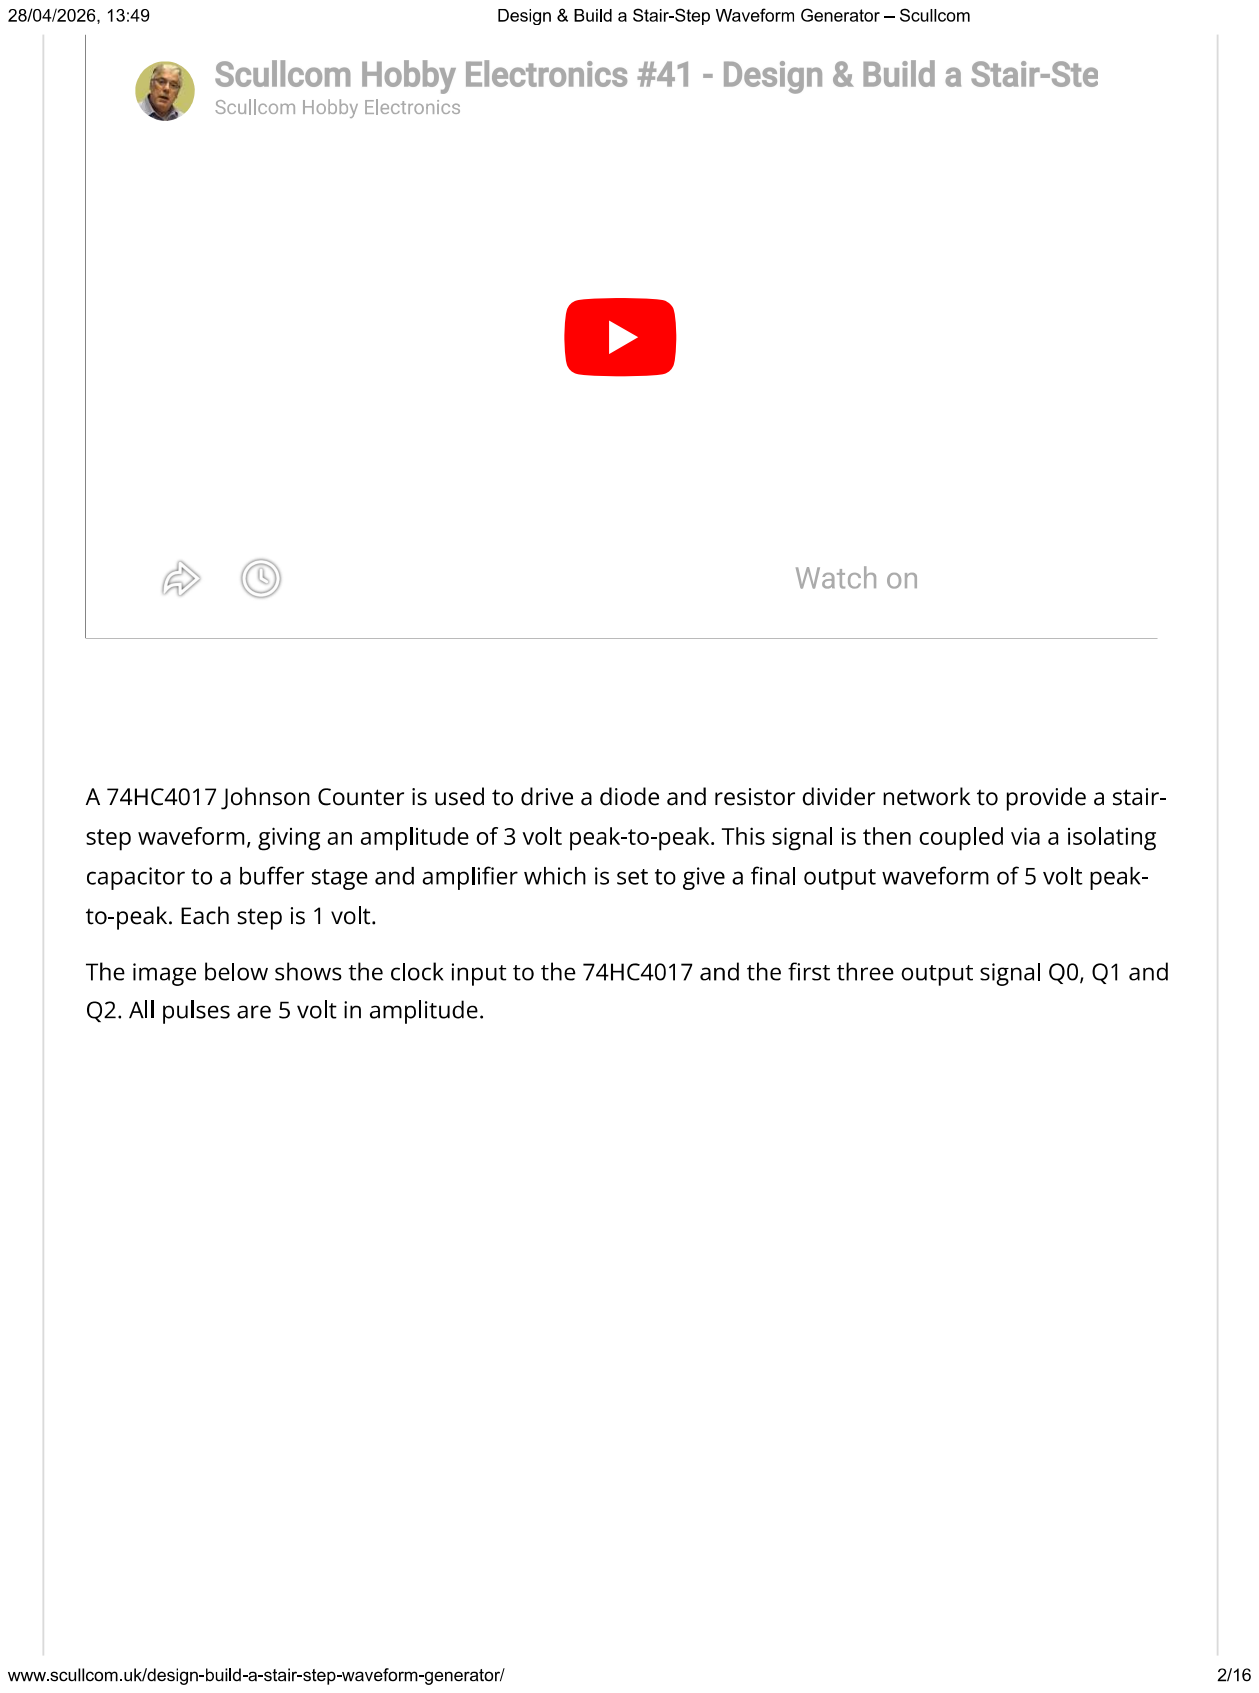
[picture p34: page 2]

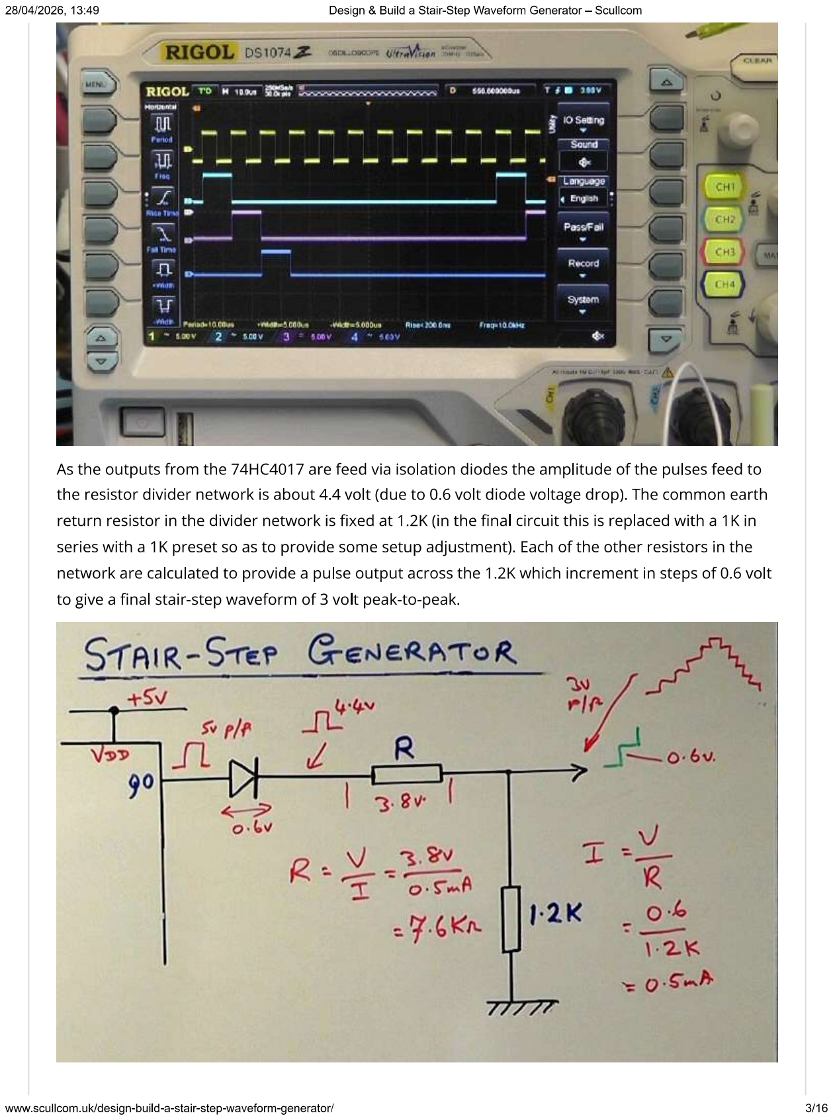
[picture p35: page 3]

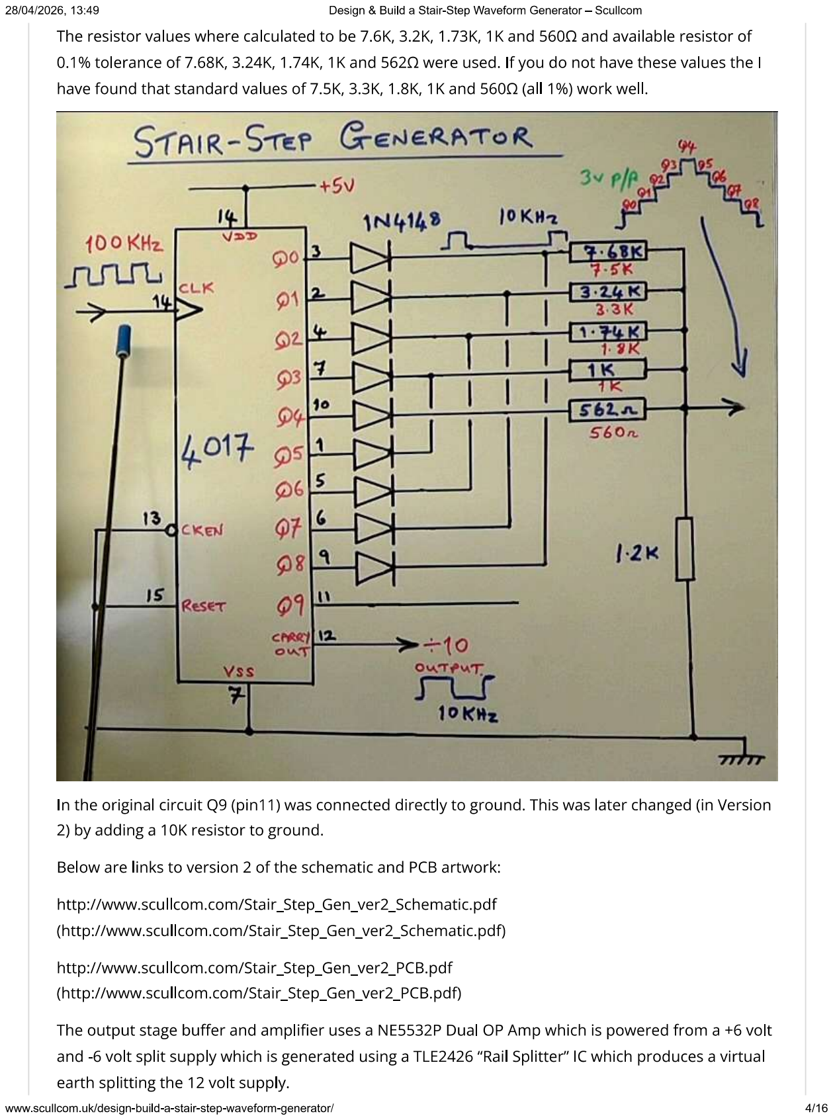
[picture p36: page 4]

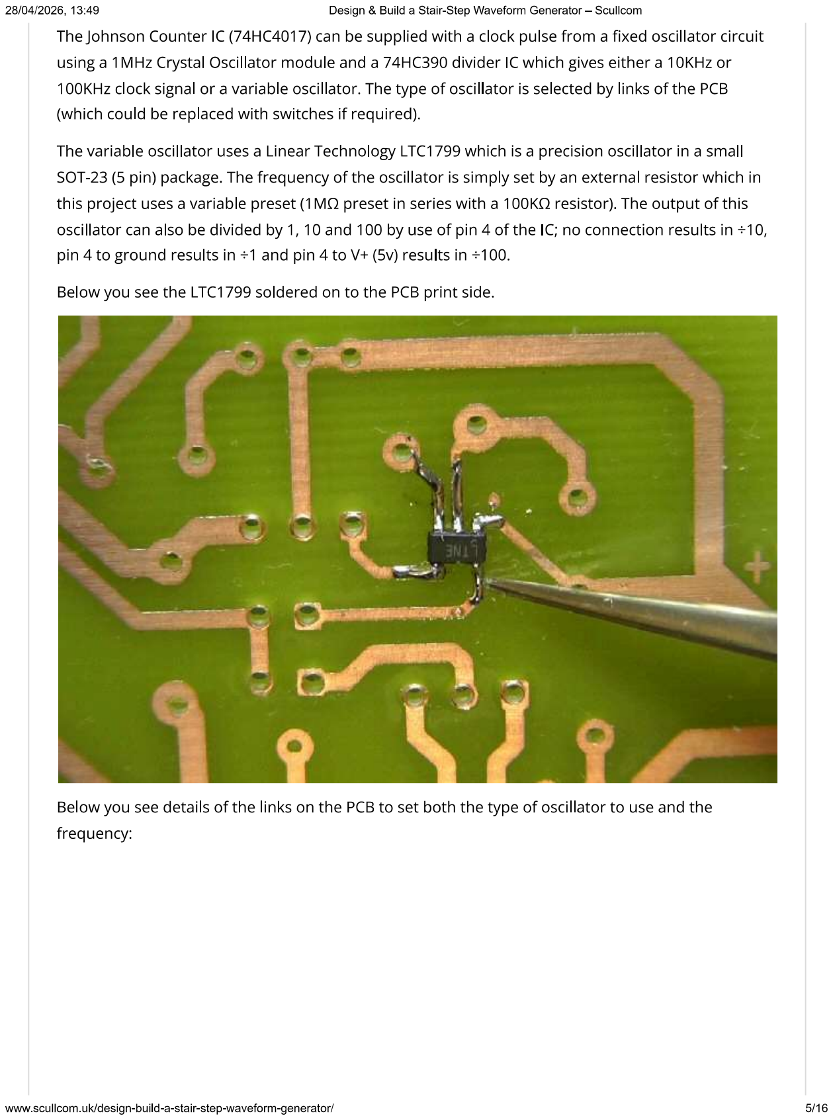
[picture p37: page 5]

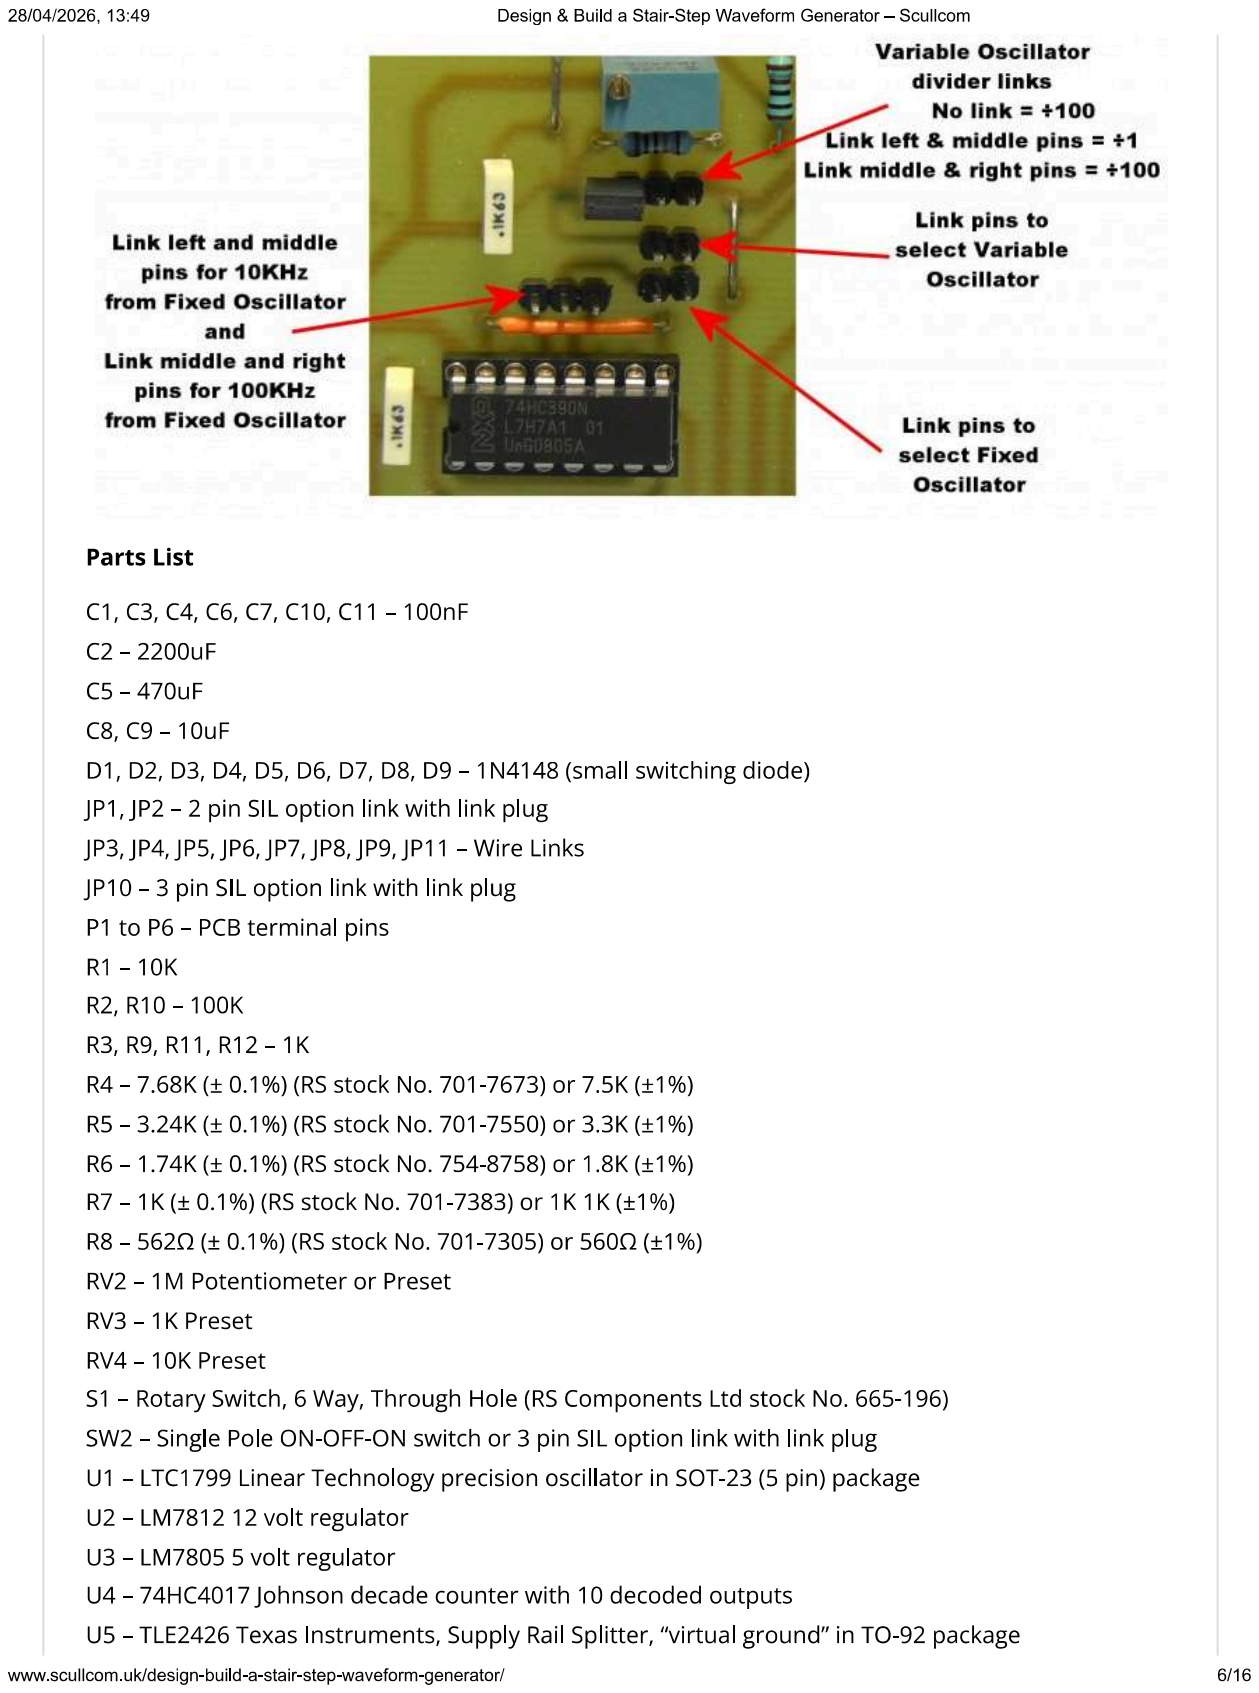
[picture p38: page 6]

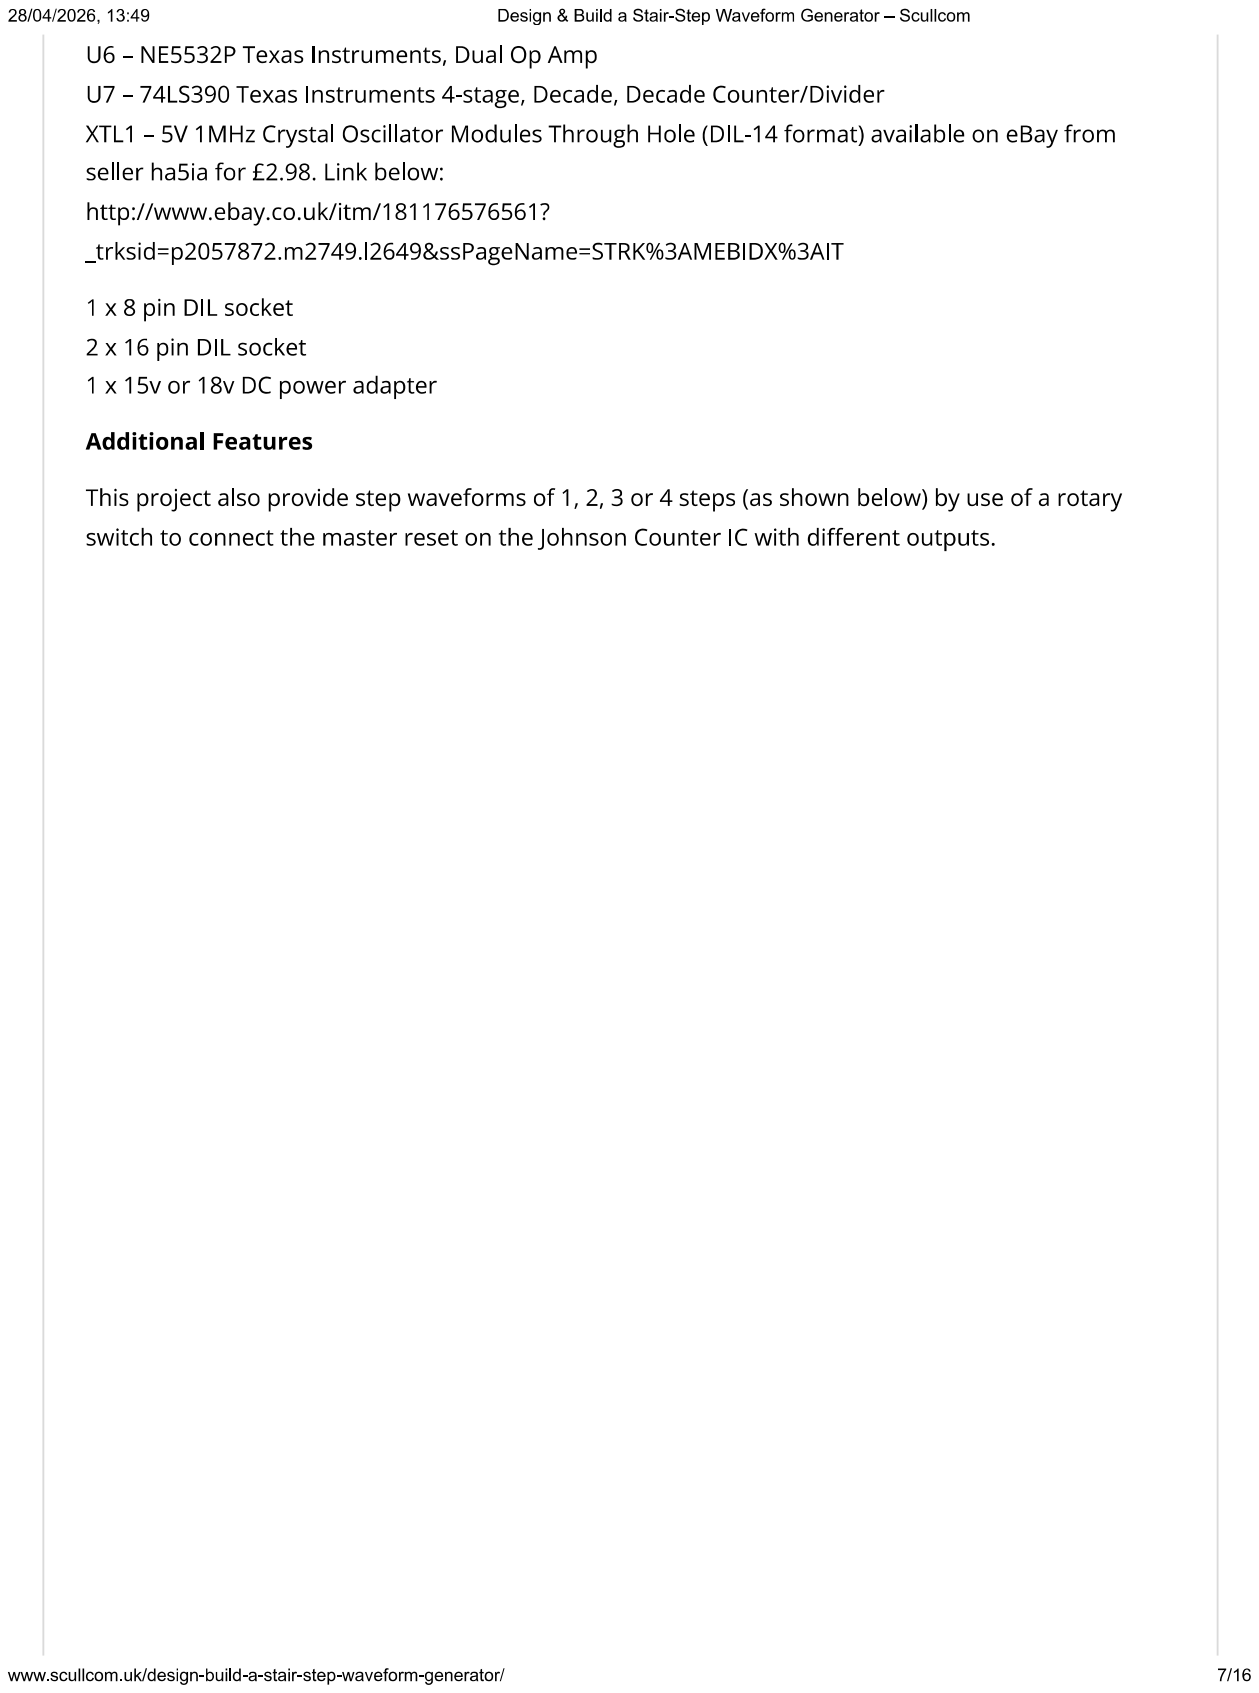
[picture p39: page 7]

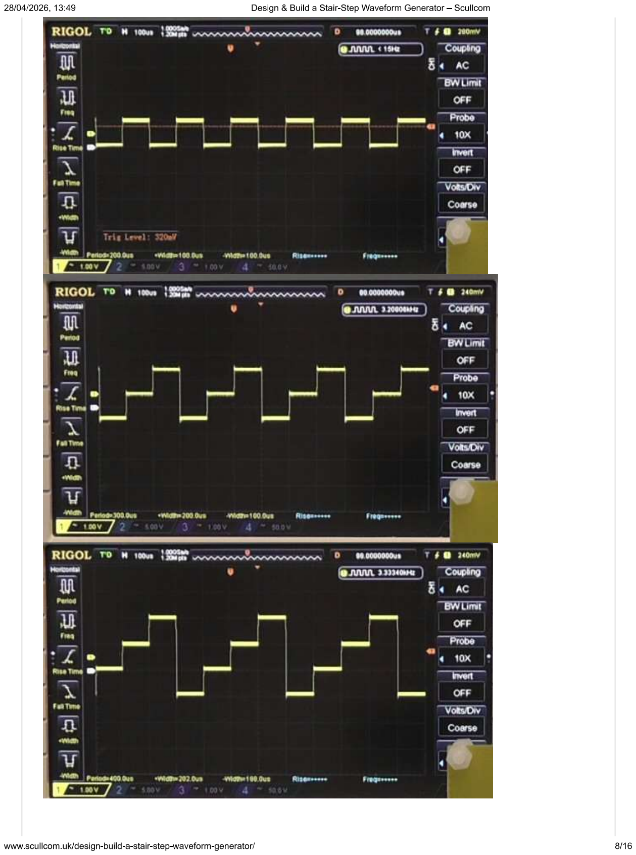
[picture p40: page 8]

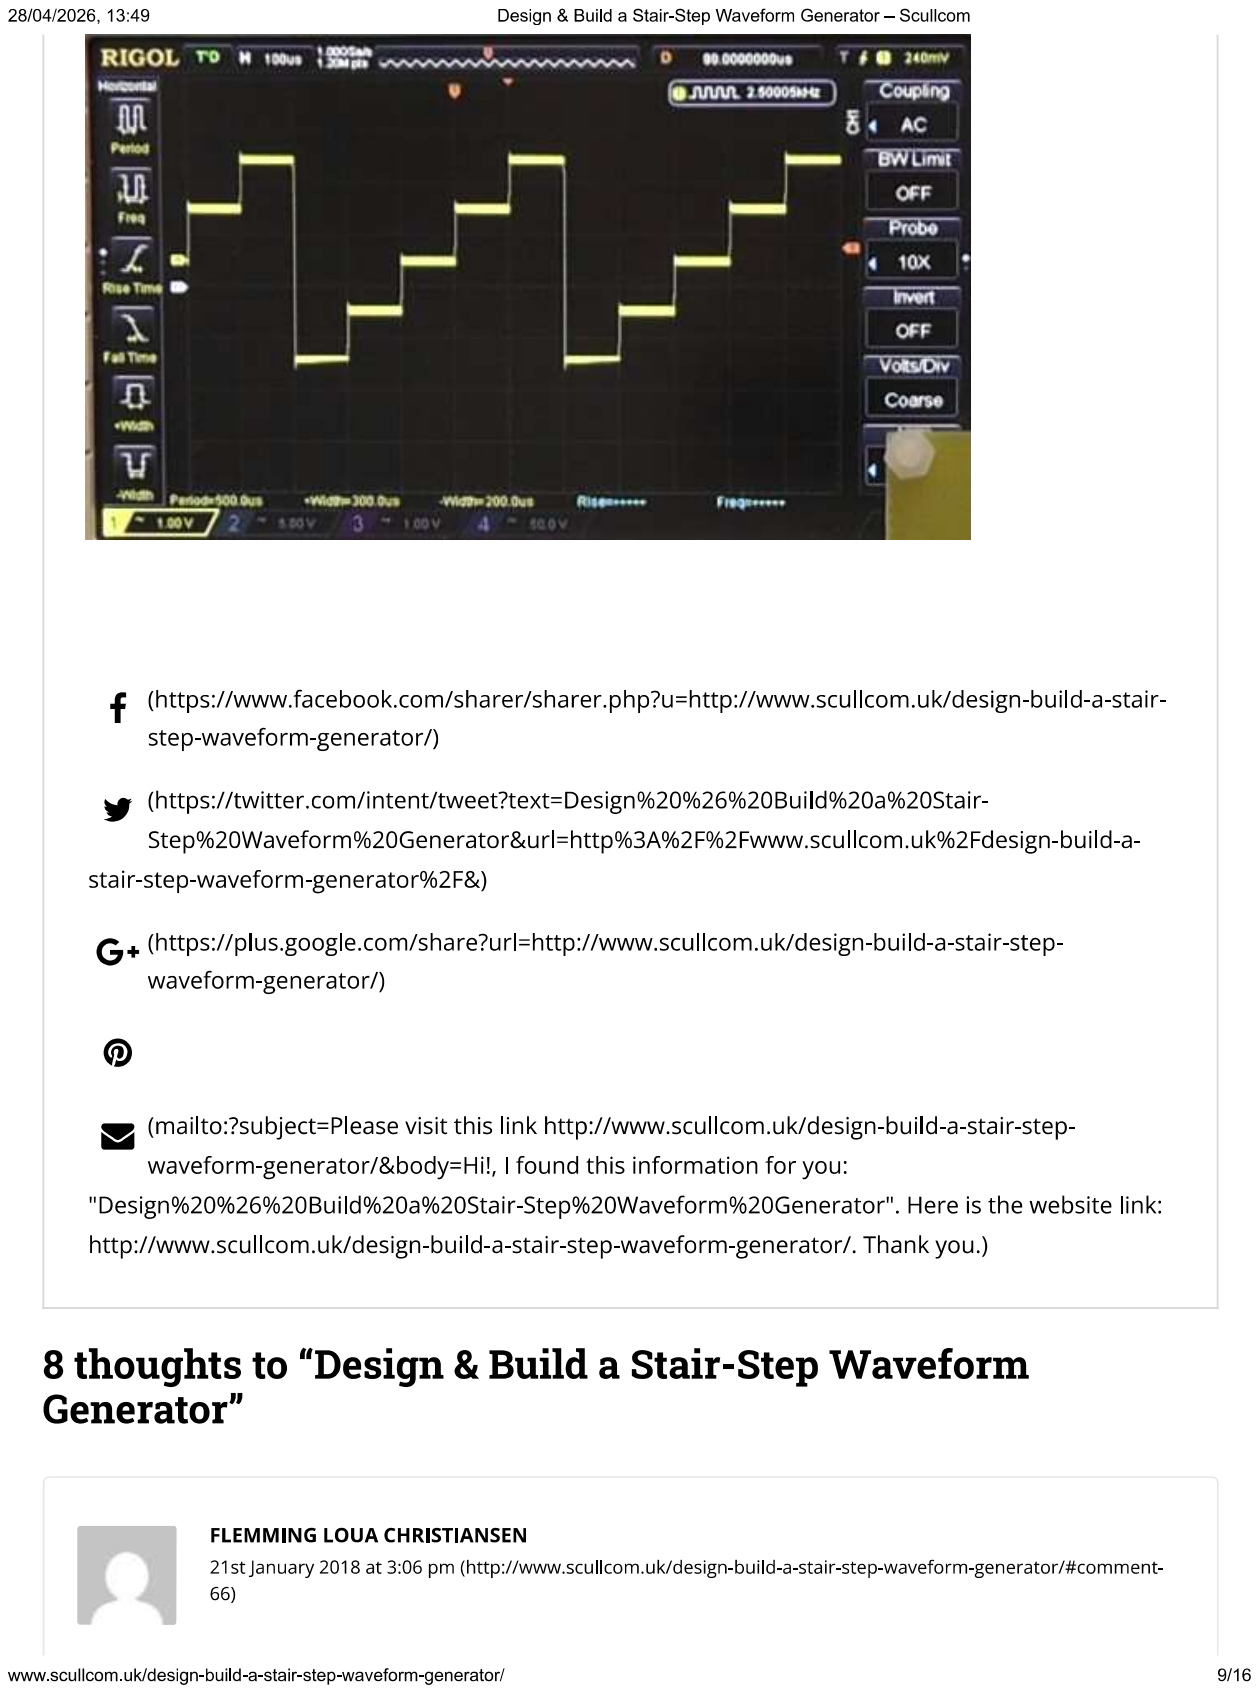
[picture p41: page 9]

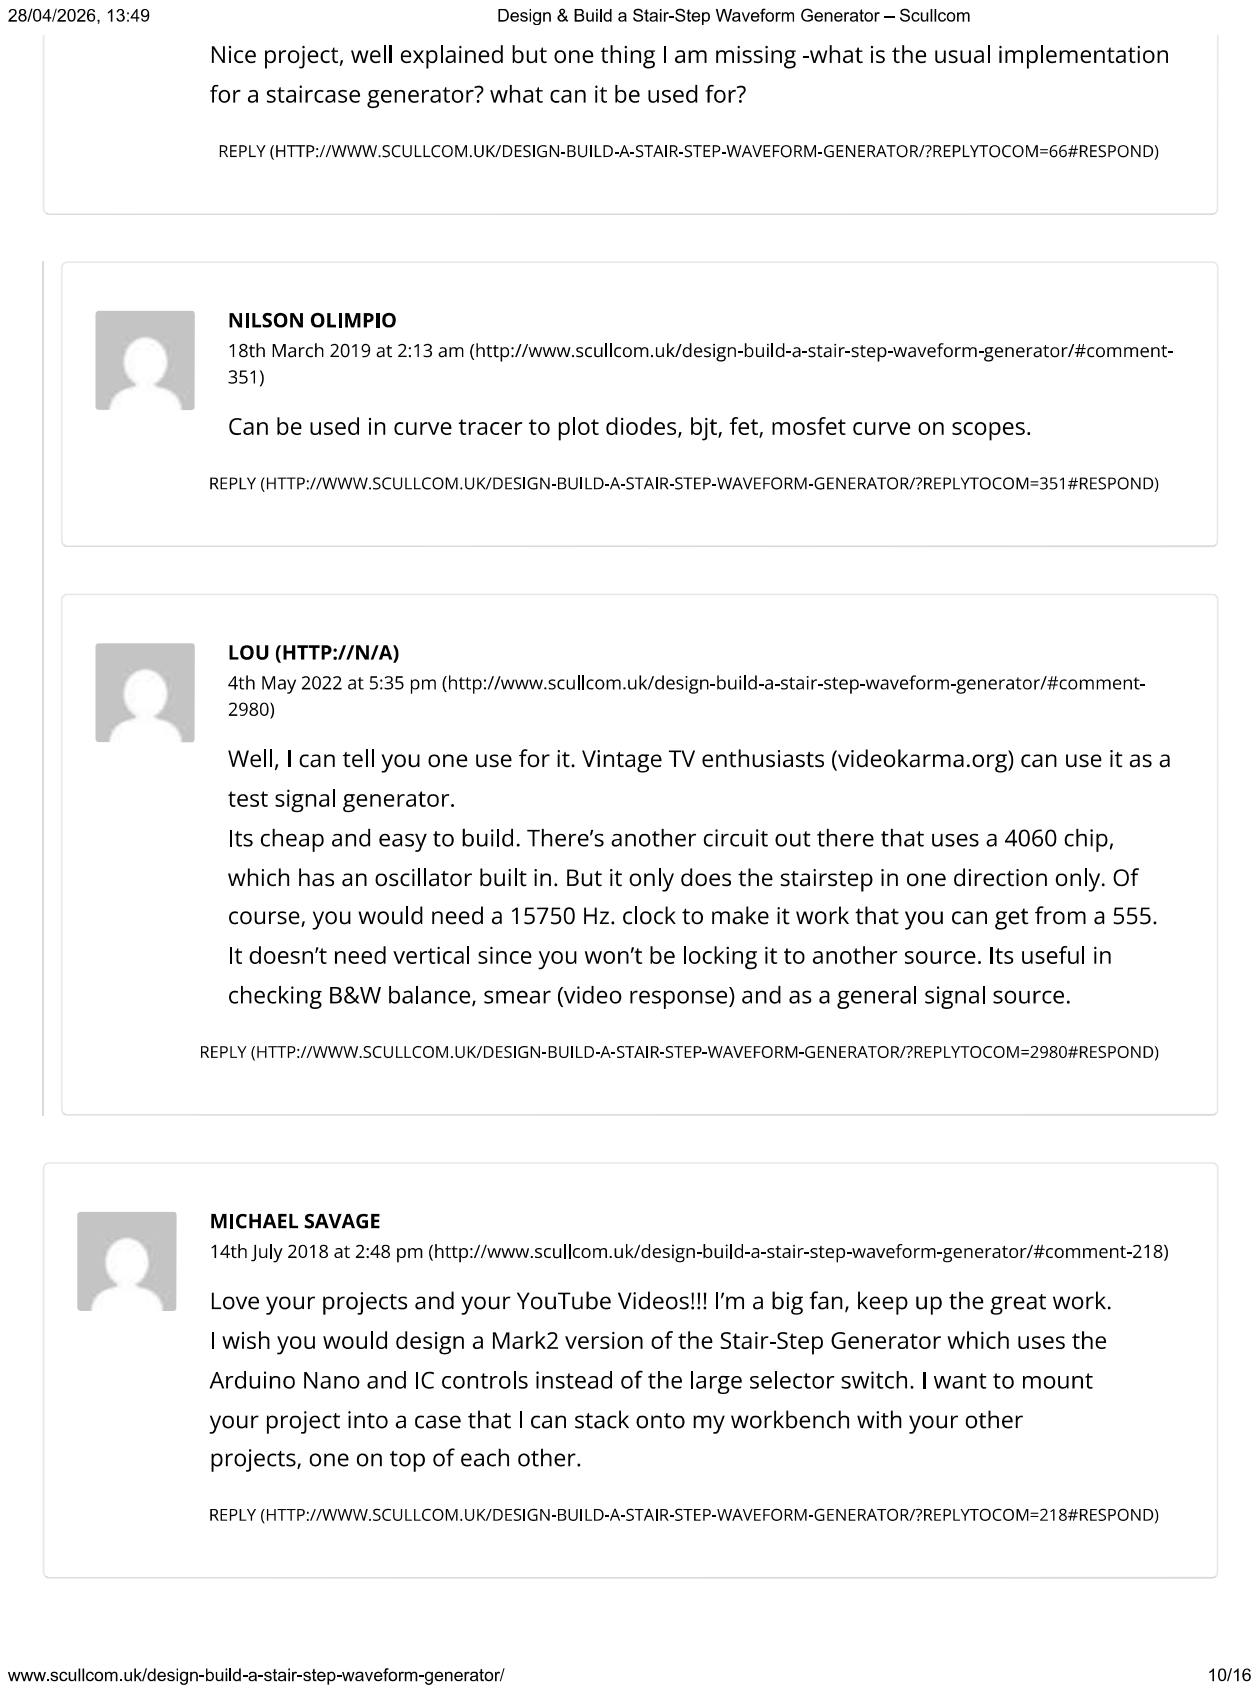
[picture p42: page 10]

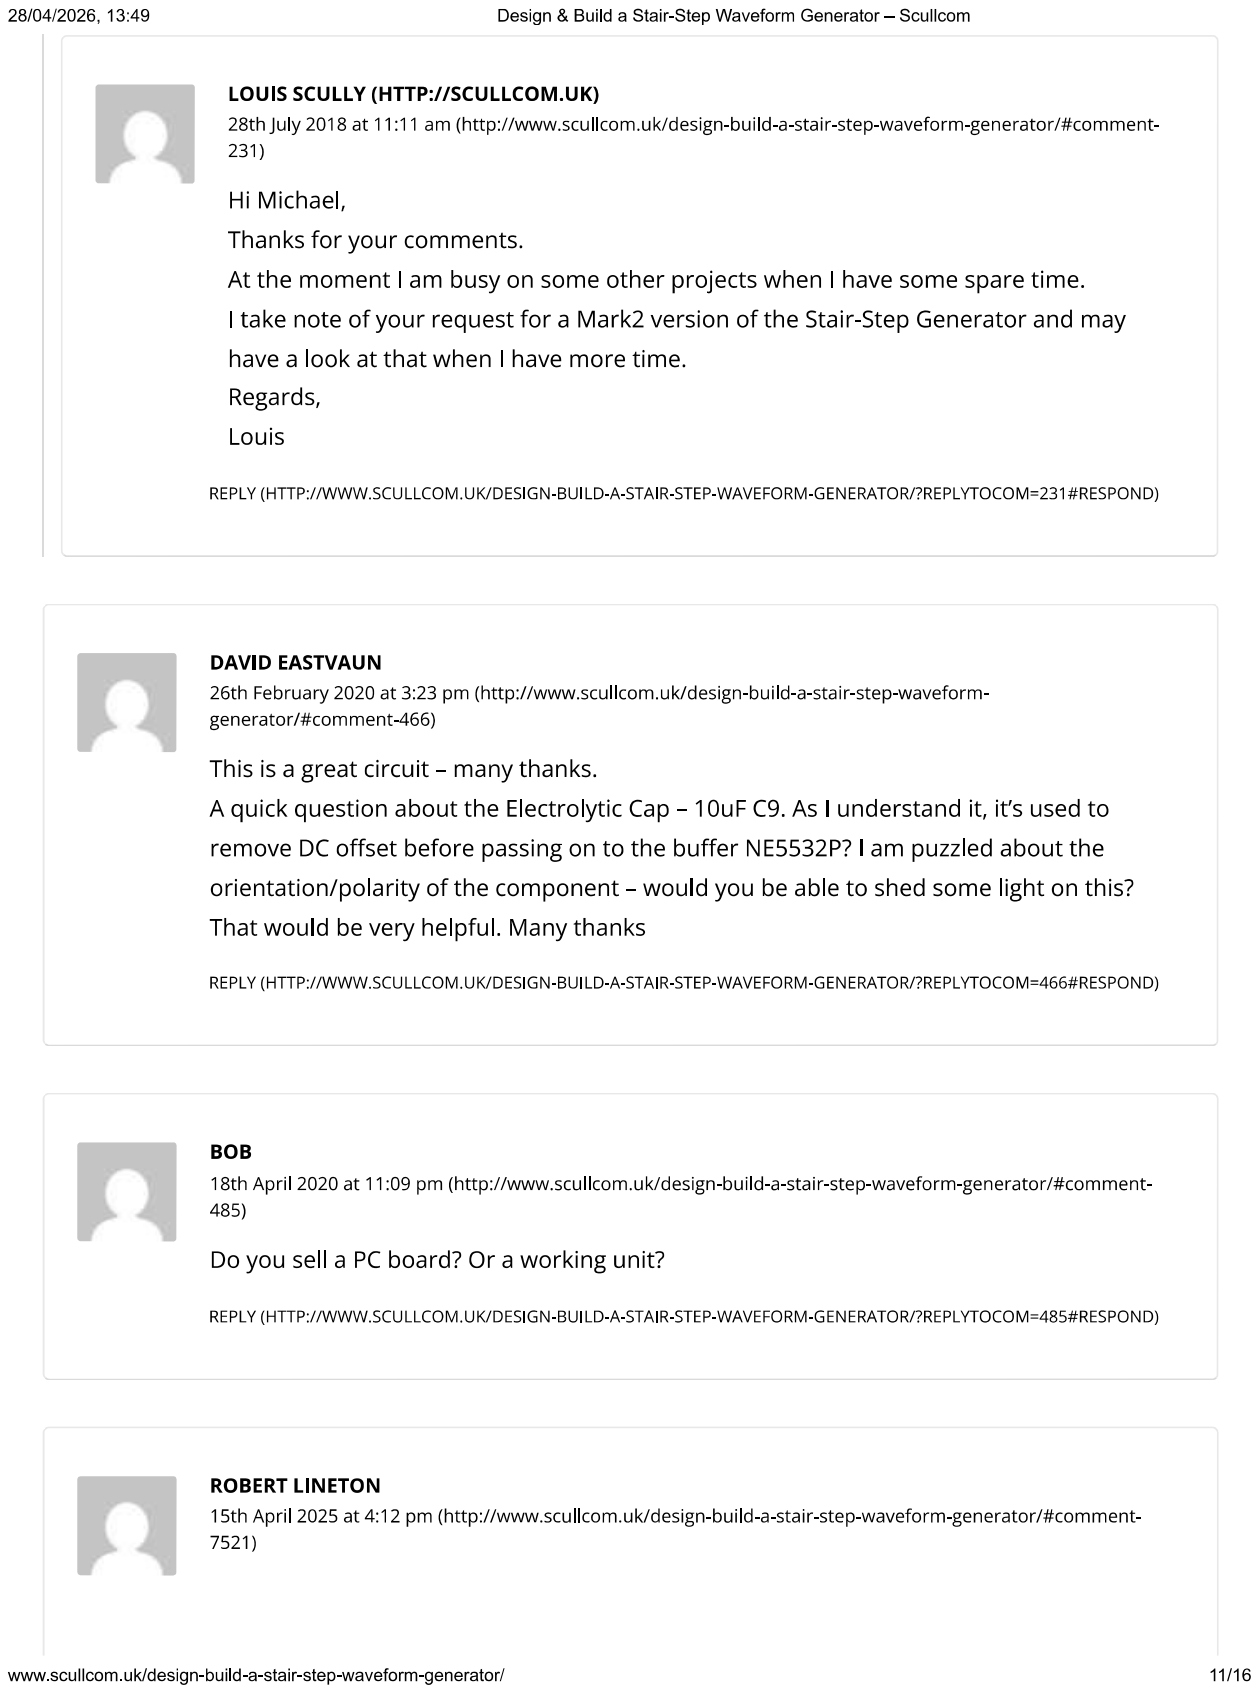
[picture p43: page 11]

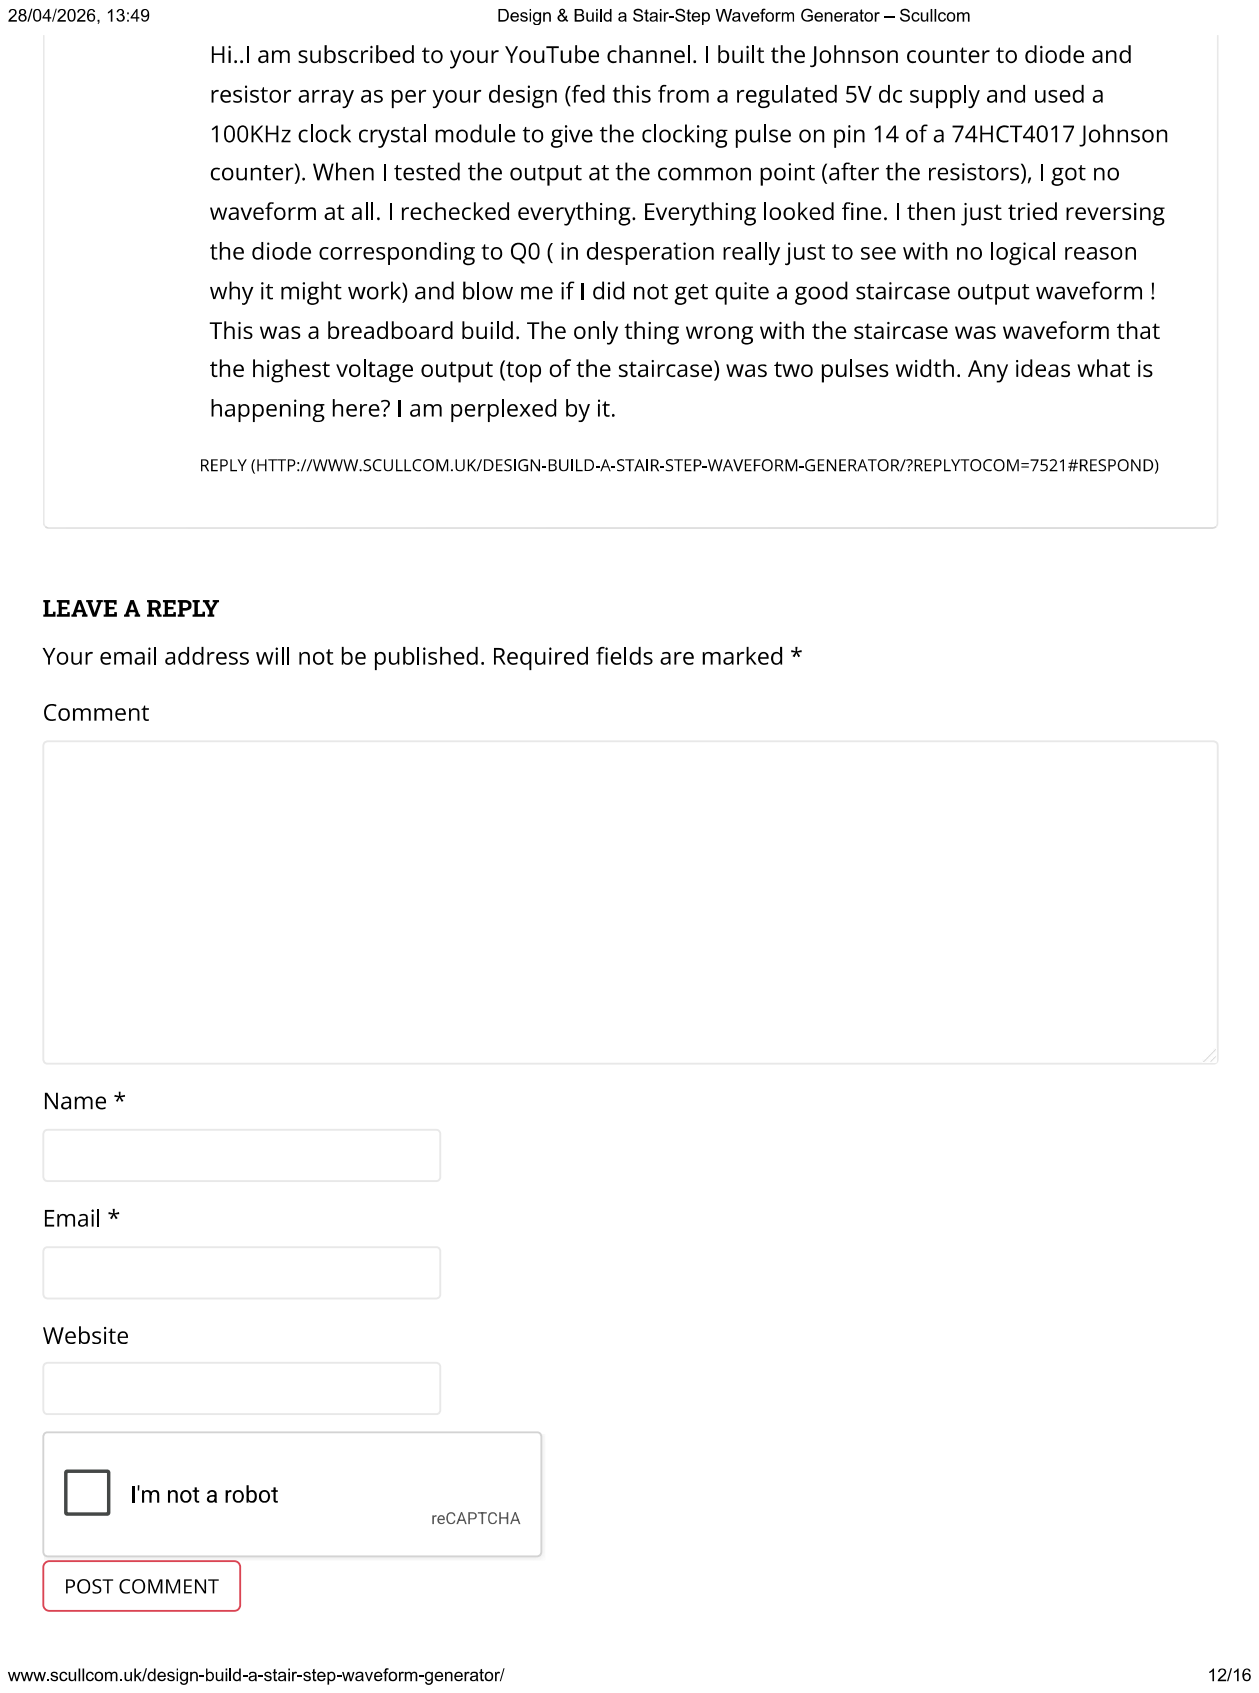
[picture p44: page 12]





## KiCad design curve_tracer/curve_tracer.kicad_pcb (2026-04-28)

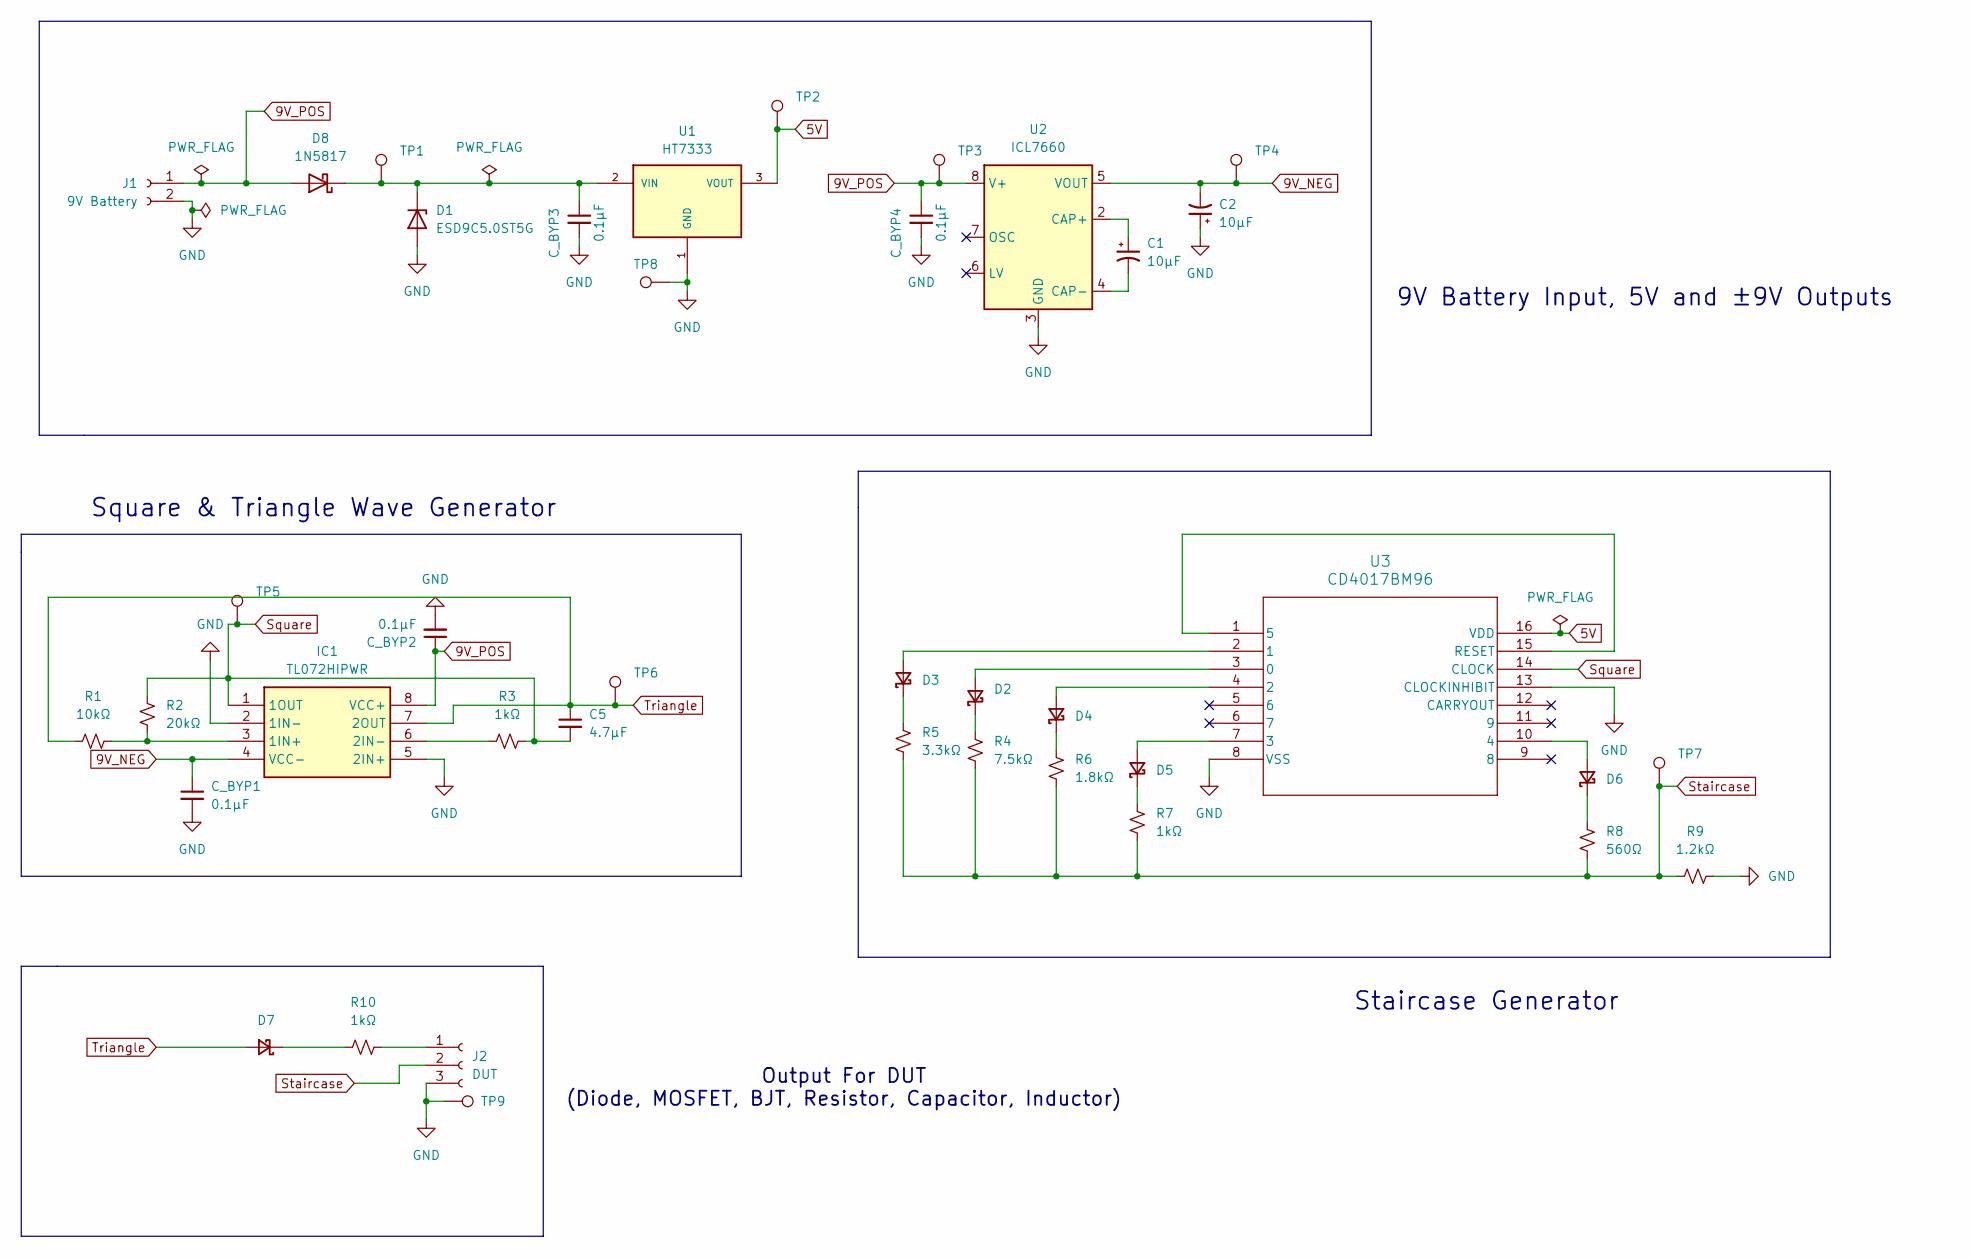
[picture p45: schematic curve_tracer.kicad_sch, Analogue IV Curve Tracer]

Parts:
C1, C2: 10μF; CP_Elec_4x5.8
C5: 4.7μF; C_0805_2012Metric
C_BYP1, C_BYP2, C_BYP3, C_BYP4: 0.1μF; C_0603_1608Metric
D1: ESD9C5.0ST5G; D_SOD-923
D2, D3, D4, D5, D6, D7: D_Schottky_Small; D_SOD-323
D8: 1N5817; D_SOD-123
IC1: TL072HIPWR; SOP65P640X120-8N; Manufacturer_Part_Number TL072HIPWR; Mouser Part Number 595-TL072HIPWR
J1: 9V Battery; BatteryHolder_MPD_BA9VPC_1xPP3
J2: DUT; PinSocket_1x03_P2.54mm_Vertical
R1: 10kΩ; R_0603_1608Metric
R2: 20kΩ; R_0603_1608Metric
R3, R7: 1kΩ; R_0603_1608Metric
R4: 7.5kΩ; R_0603_1608Metric
R5: 3.3kΩ; R_0603_1608Metric
R6: 1.8kΩ; R_0603_1608Metric
R8: 560Ω; R_0603_1608Metric
R9: 1.2kΩ; R_0603_1608Metric
R10: 1kΩ; R_Axial_DIN0207_L6.3mm_D2.5mm_P7.62mm_Horizontal
TP1, TP2, TP3, TP4, TP5, TP6, TP7, TP8, TP9: TestPoint; TestPoint_Loop_D2.50mm_Drill1.0mm_LowProfile
U1: HT7333; IC_HT7333; PARTREV 1.80
U2: ICL7660; SOIC8_4X5_INR
U3: CD4017BM96; D16

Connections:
5V: TP2.1 (1_1), U1.3 (VOUT), U3.16 (VDD)
9V_NEG: C2.2, C_BYP1.1, IC1.4 (VCC-), TP4.1 (1_1), U2.5 (VOUT)
9V_POS: C_BYP2.1, C_BYP4.1, D8.2 (A), IC1.8 (VCC+), J1.1, TP3.1 (1_1), U2.8 (V+)
GND: C2.1, C_BYP1.2, C_BYP2.2, C_BYP3.2, C_BYP4.2, D1.2 (A), IC1.2 (1IN-), IC1.5 (2IN+), J1.2, J2.3, R9.1, TP8.1 (1_1), TP9.1 (1_1), U1.1 (GND), U2.3 (GND), U3.8 (VSS), U3.13 (CLOCKINHIBIT)
unnamed: C_BYP3.1, D1.1 (K), D8.1 (K), TP1.1 (1_1), U1.2 (VIN)
unnamed: D2.2 (A), U3.3 (0)
unnamed: D2.1 (K), R4.2
unnamed: D3.2 (A), U3.2 (1)
unnamed: D3.1 (K), R5.2
unnamed: D4.2 (A), U3.4 (2)
unnamed: D4.1 (K), R6.2
unnamed: D5.2 (A), U3.7 (3)
unnamed: D5.1 (K), R7.2
unnamed: D6.2 (A), U3.10 (4)
unnamed: D6.1 (K), R8.2
unnamed: D7.1 (K), R10.1
unnamed: IC1.3 (1IN+), R1.2, R2.1
unnamed: IC1.6 (2IN-), R3.1
unnamed: J2.1, R10.2
unnamed: C1.1, U2.2 (CAP+)
unnamed: C1.2, U2.4 (CAP-)
unnamed: U3.1 (5), U3.15 (RESET)
Square: C5.2, IC1.1 (1OUT), R2.2, R3.2, TP5.1 (1_1), U3.14 (CLOCK)
Staircase: J2.2, R4.1, R5.1, R6.1, R7.1, R8.1, R9.2, TP7.1 (1_1)
Triangle: C5.1, D7.2 (A), IC1.7 (2OUT), R1.1, TP6.1 (1_1)

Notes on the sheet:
Square & Triangle Wave Generator
Staircase Generator
9V Battery Input, 5V and ±9V Outputs
Output For DUT (Diode, MOSFET, BJT, Resistor, Capacitor, Inductor)

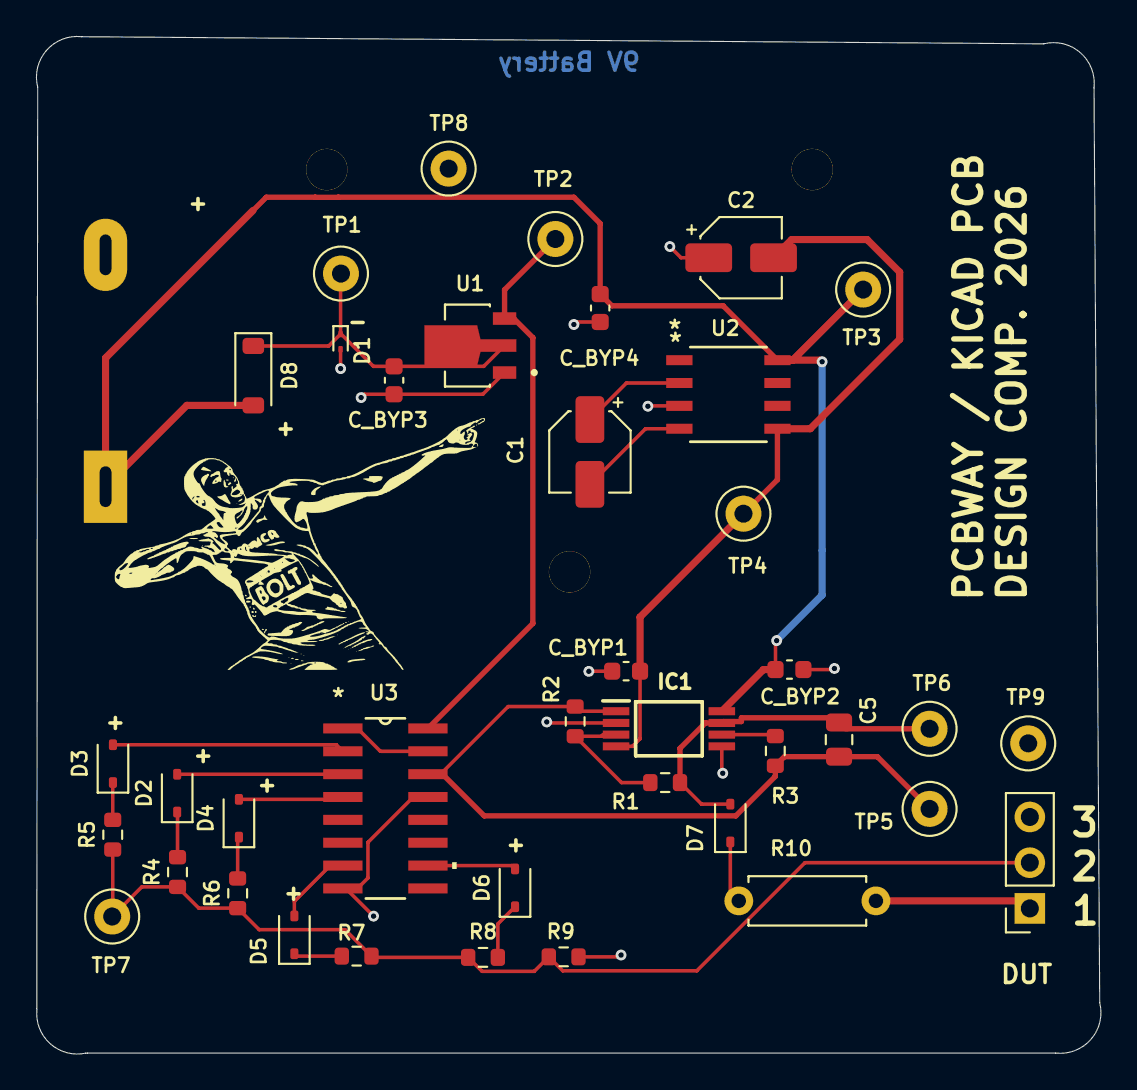
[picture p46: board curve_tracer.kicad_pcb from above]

Board: 4 copper layers, 59.1 x 56.5 mm, 40 parts (1 on the bottom side), 25 nets.
